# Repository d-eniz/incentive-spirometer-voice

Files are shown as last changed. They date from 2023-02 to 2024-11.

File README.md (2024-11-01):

# Arduino-Enabled Incentive Spirometer with Voice Feedback

This project is an Arduino-enabled incentive spirometer designed specifically for partially sighted users. It utilizes an ultrasonic sensor and the Talkie speech synthesis library to provide real-time voice feedback, making it accessible for individuals who cannot read the device. The system measures the user's inhalation speed and provides audio instructions to encourage effective use.

## Features

- Measures inhalation speed using an ultrasonic sensor.
- Provides voice feedback:
  - **"Safe Speed"** when the inhalation rate is stable.
  - **"Slow Down"** if the inhalation is too fast.
  - **"Speed Up"** if the inhalation is too slow.
- Easy-to-read documentation and making instructions included.

## Hardware Requirements

- Arduino board
- Ultrasonic sensor (HC-SR04 or similar)
- Button (for triggering measurements)
- Speaker (for voice output)
- Talkie library (included in the code for voice synthesis)

Detailed hardware requirements can be found in the [making instructions](./documentation/Making%20Instructions.pdf).

## Installation

1. Clone or download the repository to your local machine.
2. Ensure you have the [Talkie](https://github.com/going-digital/Talkie) library installed in your Arduino IDE.
3. Connect the components as follows:
   - **Trigger Pin**: Digital pin 11
   - **Echo Pin**: Digital pin 12
   - **Switch Pin**: Digital pin 2 (configured with internal pull-up)
4. Upload the code to your Arduino board.

## Usage

1. Press the button connected to `switchPin` to start the spirometer.
2. The system will begin measuring inhalation speed and providing verbal feedback.
3. Based on the inhalation speed, the system will announce:
   - "Safe Speed" when the inhalation is at an appropriate rate.
   - "Slow Down" if the inhalation is too fast.
   - "Speed Up" if the inhalation is too slow.

4. View additional information in the included easy-read guide and follow the audio user instructions for further assistance.

## Documentation

Comprehensive documentation is available, including:
- [Making instructions](./documentation/Making%20Instructions.pdf) for assembly and setup.
- An [easy-read guide](./documentation/Easy%20Read%20guide.pdf) for understanding the device and its use.
- [Audio user instructions](./documentation/Audio%20User%20instructions.mp3) for hands-on support.

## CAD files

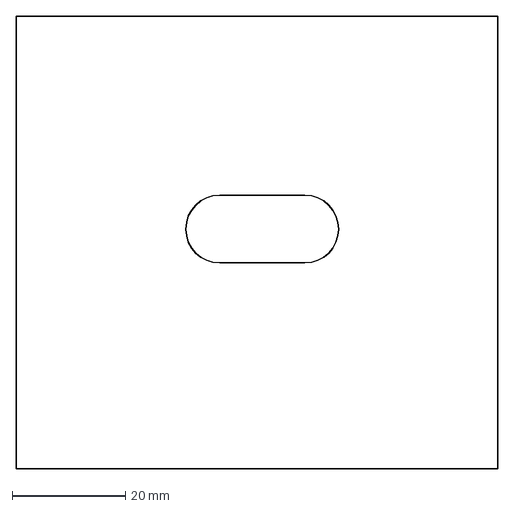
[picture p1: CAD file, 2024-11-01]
dxf/Speaker side.dxf
85.0 x 80.0 mm

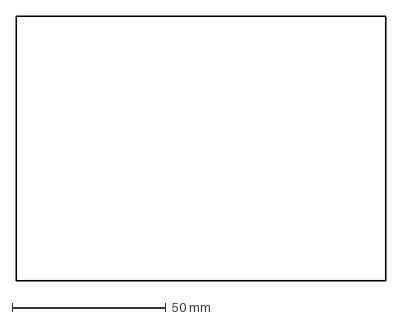
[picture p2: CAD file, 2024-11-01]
dxf/Rectangle sides.dxf
120.0 x 86.0 mm

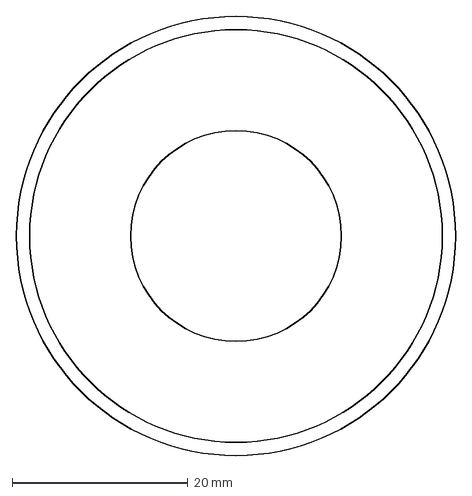
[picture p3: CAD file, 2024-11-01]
dxf/Chamber acrylic donut.dxf
50.0 x 50.0 mm

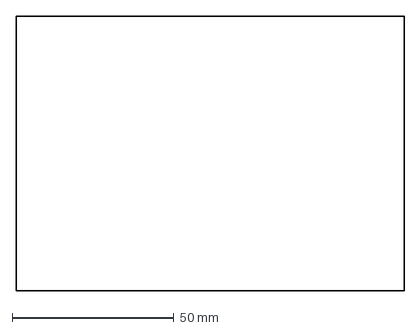
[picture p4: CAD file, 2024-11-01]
dxf/Bottom.dxf
120.0 x 85.0 mm

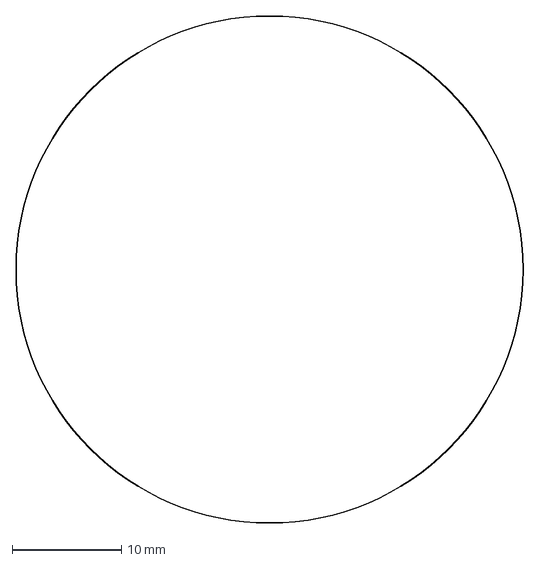
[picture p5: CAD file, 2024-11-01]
dxf/Disc.dxf
46.5 x 46.5 mm

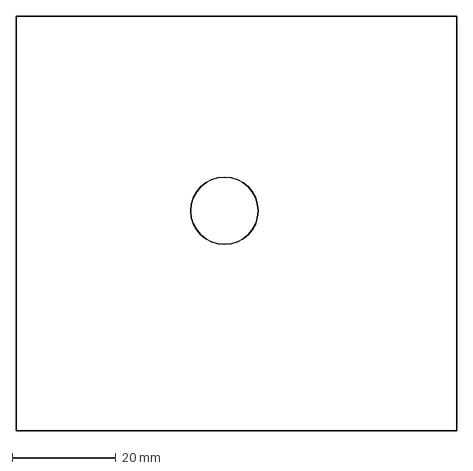
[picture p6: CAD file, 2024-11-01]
dxf/Switch side.dxf
85.0 x 80.0 mm

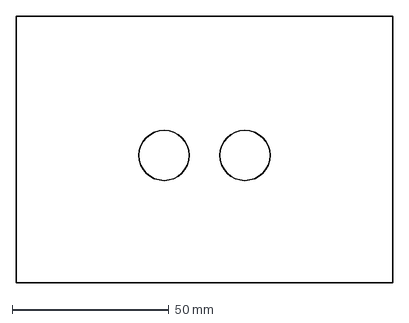
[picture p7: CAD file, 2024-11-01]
dxf/Lid.dxf
120.0 x 85.0 mm

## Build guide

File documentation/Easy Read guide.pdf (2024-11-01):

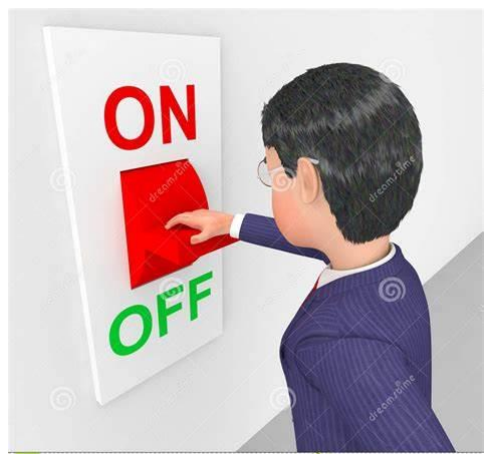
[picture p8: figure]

Switch on the device.

The switch can be found
attached to the black box.

If the device beeps, it is on.

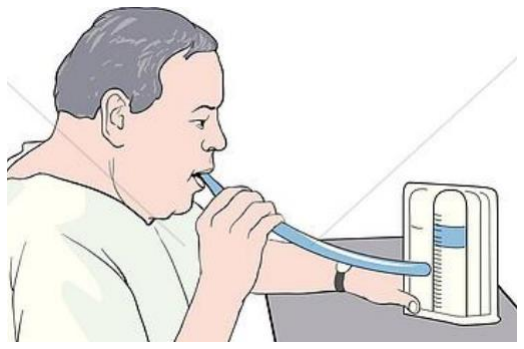
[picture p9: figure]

Place lips on the mouthpiece.

Wait for the voice to say “start”.

Then breathe in for 4 seconds.

Inhale at a steady rate for 4 seconds.

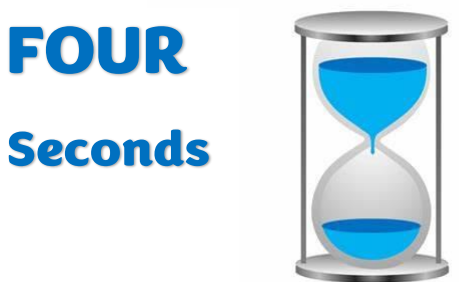
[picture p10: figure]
FOUR; Seconds

After 4 seconds another voice should be heard.

The audio will state the volume of air inhaled in millilitres.

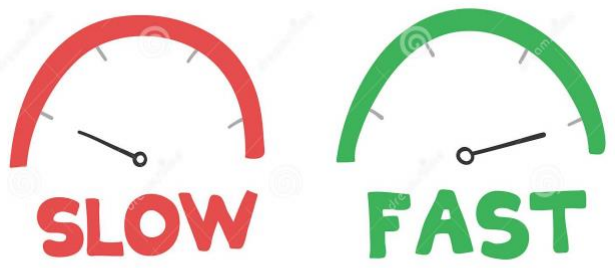
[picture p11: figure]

After this another audio will be heard.

Slow breathing = “speed up”

Steady Breathing = “safe speed”

Fast breathing = “slow down”

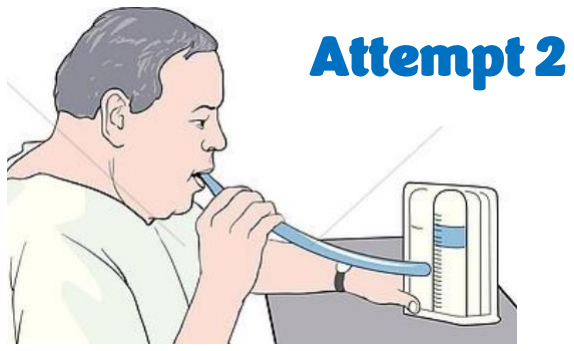
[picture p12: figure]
Attempt 2

If your result was not “safe speed” you can try again.

If the result was “too slow” try and breathe in faster.

If the result was “too fast” try and breath in slower.

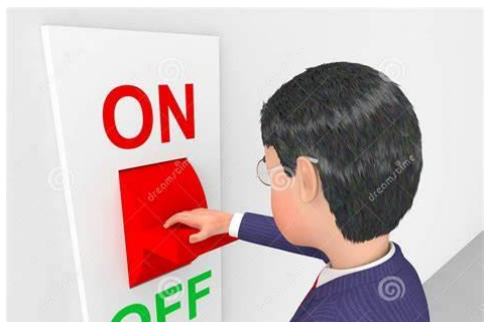
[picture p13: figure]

When finished using, switch off the device.

The switch button is attached to the black box.

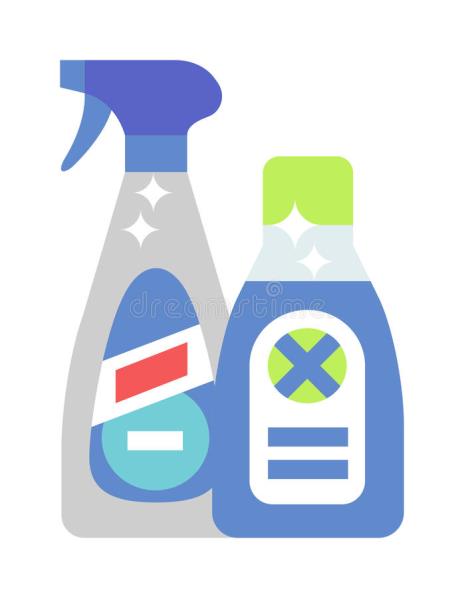
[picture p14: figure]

After finished using, clean the mouthpiece.

Do this by taking out the flexible mouthpiece from the lid.

Use disinfected solution to rinse the mouthpiece for 15 minutes.

Wait for this to dry.

Wipe the device with alcohol wipes.

Do this to remove bacteria.

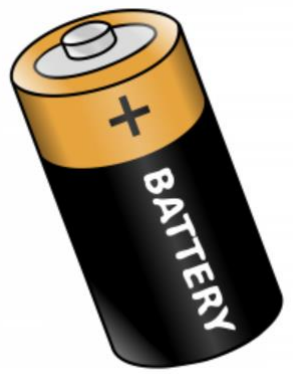
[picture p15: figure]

When the battery runs out
replace it.

Do this by removing the present battery found in the black box.

Then place in the new battery.

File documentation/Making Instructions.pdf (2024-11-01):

Part 1 - CAD
1.1 - Download all provided DXF files.
1.2 - Upload the DXF files to Illustrator and modify them so that all outlines are red and 0.001mm thick - then, print to laser cutting software. The following pieces should be cut:
- Bottom x 1
- Lid x 1
- Chamber acrylic donut x 1
- Rectangle sides x 2
- Speaker side x 1
- Switch side x 1
- Disc x 6

Part 2 - Electronics and Software

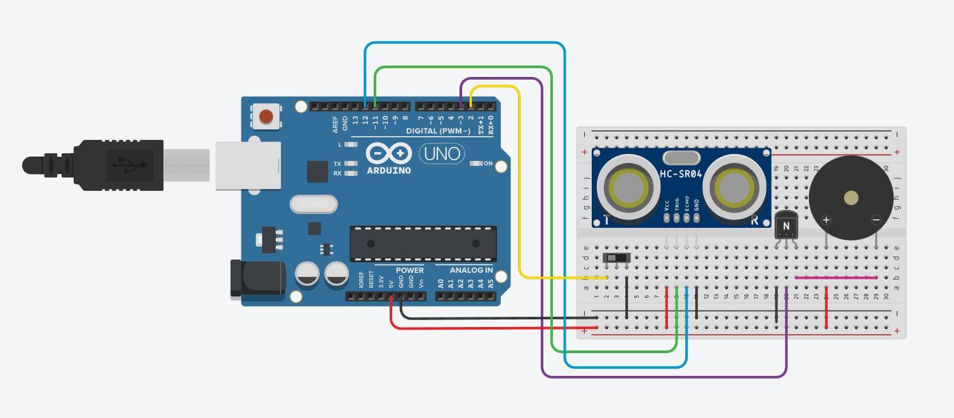
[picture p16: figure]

Required materials:
- Computer with Arduino IDE installed
- Arduino Uno
- Breadboard
- Wires
- HC-SR04 Ultrasonic Distance Sensor
- Speaker driver
- NPN transistor
- Toggle switch
- 9V battery and adapter
- USB type A to B cable

2.1 - Use the circuit diagram and connect every component to the breadboard accordingly. 2.2 - Connect Arduino Uno into computer and run Arduino IDE.
2.3 - Download Talkie: https://github.com/adafruit/Talkie
2.4 - Click Sketch > Include Library > Add .ZIP Library… and choose Talkie-master.zip 2.5 - Copy the following code and paste into Arduino IDE.

2.6 - Copy code version 3.2.0 from the following repository: https://github.com/aribaza/scenario-6/blob/main/V3.2.0
2.6 - Upload the code into the board. Once uploaded, disconnect the Arduino Uno.

Part 3 - Manufacturing
Required materials:
- Laser cutter
- Hack saw
- Saw workbench with clamps
- Hot glue gun
- Epoxy resin
- Scissors
- Sandpaper
- Velcro strips
- Opaque 3mm acrylic plate
- GEVACRIL D=50x47mm L=2000mm Polycarbonate Tube
- Flexible PVC pipe
3.1 - Retrieve laser cut pieces from step 1.
3.2 - The laser cutter will have cut six identical discs. Stack the discs individually, applying a very thin layer of hot glue between them. There should ideally be no spacing between each disc layer. Secure the discs with clamps and let them dry, ensuring that the discs are aligned and don’t stick out. Once cooled, sand the edges.
3.3 - Assemble the box in reference to the CAD file. Use hot glue to seal the edges. Leave out one of the 120x85mm “Rectangle sides.dxf” side plates for now.
3.4 - Cut four 3x120mm velcro strips and stick them on the open side of the box and the remaining plate. This should allow for the side plate to detach and reattach.
3.5 - Get GEVACRIL D=50x47mm L=2000mm Polycarbonate Tube. Using a ruler measure out the 28cm point from the edge and mark it along the tube using a pen. Clamp the tube and cut through the mark. Sand down the sharp edge of the new 28cm tube using sandpaper.
3.6 - Using epoxy resin, join the acrylic disc piece with the hole to the 28cm tube.
3.7 - Place the stacked disks inside the tube, and join the empty side of the tube with the top part of the box. Centre the two holes in the acrylic plate with the tube.
3.8 - Using hot glue, secure the ultrasonic sensor in the box. The receiver and the emitter of the sensor should be sticking up to the tube from the holes in the acrylic plates.
3.9 - Using hot glue, secure the speaker in the oval hole in the side of the box.
3.10 - Unscrew the nut on the toggle switch, stick the switch from inside of the box through the the designated hole on the side of the box and secure from the outside using the nut.,
3.11 - Put the 9V battery into the adapter and connect the adapter to the Arduino.
3.12 - Insert flexible mouth tube into acrylic donut

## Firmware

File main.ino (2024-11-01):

#include "talkie.h"

int trigPin = 11;    // Trigger
int echoPin = 12;    // Echo
long duration, cm, inches;
const int switchPin = 2;
int switchState = HIGH;

Talkie voice;


const uint8_t sp0[] PROGMEM = {0x69,0xFB,0x59,0xDD,0x51,0xD5,0xD7,0xB5,0x6F,0x0A,0x78,0xC0,0x52,0x01,0x0F,0x50,0xAC,0xF6,0xA8,0x16,0x15,0xF2,0x7B,0xEA,0x19,0x47,0xD0,0x64,0xEB,0xAD,0x76,0xB5,0xEB,0xD1,0x96,0x24,0x6E,0x62,0x6D,0x5B,0x1F,0x0A,0xA7,0xB9,0xC5,0xAB,0xFD,0x1A,0x62,0xF0,0xF0,0xE2,0x6C,0x73,0x1C,0x73,0x52,0x1D,0x19,0x94,0x6F,0xCE,0x7D,0xED,0x6B,0xD9,0x82,0xDC,0x48,0xC7,0x2E,0x71,0x8B,0xBB,0xDF,0xFF,0x1F};
const uint8_t sp1[] PROGMEM = {0x66,0x4E,0xA8,0x7A,0x8D,0xED,0xC4,0xB5,0xCD,0x89,0xD4,0xBC,0xA2,0xDB,0xD1,0x27,0xBE,0x33,0x4C,0xD9,0x4F,0x9B,0x4D,0x57,0x8A,0x76,0xBE,0xF5,0xA9,0xAA,0x2E,0x4F,0xD5,0xCD,0xB7,0xD9,0x43,0x5B,0x87,0x13,0x4C,0x0D,0xA7,0x75,0xAB,0x7B,0x3E,0xE3,0x19,0x6F,0x7F,0xA7,0xA7,0xF9,0xD0,0x30,0x5B,0x1D,0x9E,0x9A,0x34,0x44,0xBC,0xB6,0x7D,0xFE,0x1F};
const uint8_t sp2[]  PROGMEM = {0x06,0xB8,0x59,0x34,0x00,0x27,0xD6,0x38,0x60,0x58,0xD3,0x91,0x55,0x2D,0xAA,0x65,0x9D,0x4F,0xD1,0xB8,0x39,0x17,0x67,0xBF,0xC5,0xAE,0x5A,0x1D,0xB5,0x7A,0x06,0xF6,0xA9,0x7D,0x9D,0xD2,0x6C,0x55,0xA5,0x26,0x75,0xC9,0x9B,0xDF,0xFC,0x6E,0x0E,0x63,0x3A,0x34,0x70,0xAF,0x3E,0xFF,0x1F};
const uint8_t sp3[] PROGMEM = {0x0C,0xE8,0x2E,0x94,0x01,0x4D,0xBA,0x4A,0x40,0x03,0x16,0x68,0x69,0x36,0x1C,0xE9,0xBA,0xB8,0xE5,0x39,0x70,0x72,0x84,0xDB,0x51,0xA4,0xA8,0x4E,0xA3,0xC9,0x77,0xB1,0xCA,0xD6,0x52,0xA8,0x71,0xED,0x2A,0x7B,0x4B,0xA6,0xE0,0x37,0xB7,0x5A,0xDD,0x48,0x8E,0x94,0xF1,0x64,0xCE,0x6D,0x19,0x55,0x91,0xBC,0x6E,0xD7,0xAD,0x1E,0xF5,0xAA,0x77,0x7A,0xC6,0x70,0x22,0xCD,0xC7,0xF9,0x89,0xCF,0xFF,0x03};
const uint8_t sp4[] PROGMEM = {0x08,0x68,0x21,0x0D,0x03,0x1C,0x90,0xC0,0x88,0x92,0xB2,0x29,0x87,0x76,0x2B,0x2D,0x5C,0x7B,0x06,0xD9,0xED,0x74,0x64,0x51,0x54,0x4D,0xA2,0xBA,0x99,0xB7,0x3A,0xF8,0xEA,0x74,0xCA,0xD3,0x87,0xBE,0x94,0x3D,0xA4,0xD4,0x4E,0xC9,0x5F,0xF7,0x72,0xA7,0x9C,0x1C,0x63,0xDE,0xF2,0x9B,0xBE,0x34,0x84,0x27,0x2D,0x4B,0xF8,0x53,0x09,0x9C,0x0E,0xB7,0xEE,0xCB,0x5B,0x70,0xDD,0xB2,0xFC,0x3F};
const uint8_t sp5[] PROGMEM = {0x08,0x68,0x4E,0x9D,0x02,0x1C,0x60,0xC0,0x8C,0x69,0x12,0xB0,0xC0,0x28,0xAB,0x8C,0x9C,0xC0,0x2D,0xBB,0x38,0x79,0x31,0x15,0xA3,0xB6,0xE4,0x16,0xB7,0xDC,0xF5,0x6E,0x57,0xDF,0x54,0x5B,0x85,0xBE,0xD9,0xE3,0x5C,0xC6,0xD6,0x6D,0xB1,0xA5,0xBF,0x99,0x5B,0x3B,0x5A,0x30,0x09,0xAF,0x2F,0xED,0xEC,0x31,0xC4,0x5C,0xBE,0xD6,0x33,0xDD,0xAD,0x88,0x87,0xE2,0xD2,0xF2,0xF4,0xE0,0x16,0x2A,0xB2,0xE3,0x63,0x1F,0xF9,0xF0,0xE7,0xFF,0x01};
const uint8_t sp6[] PROGMEM = {0x04,0xF8,0xB9,0x55,0x01,0xBF,0xA5,0x1B,0xE0,0x37,0x0F,0x03,0xFC,0x96,0x61,0x80,0xDF,0x3C,0x0C,0xF0,0x93,0xDA,0x4A,0x87,0x49,0x53,0x91,0x37,0x2B,0x6D,0xD2,0x55,0x23,0xDE,0xAC,0xAA,0xB9,0x16,0x09,0xFF,0xB2,0xFA,0x66,0x93,0x3C,0x63,0xF3,0x9C,0x10,0x38,0x45,0xA9,0x0A,0xD5,0x00,0x00,0x02,0x14,0x97,0xAA,0x80,0xAB,0x6B,0x0D,0xF0,0x63,0xA5,0x01,0x7E,0xCB,0x30,0xC0,0x6F,0xE9,0x0A,0xF8,0x25,0x93,0x01,0x3F,0x57,0xFC,0x3F};
const uint8_t sp7[] PROGMEM = {0x0C,0x78,0xC6,0x95,0x01,0x3F,0xA5,0x28,0xE0,0xB7,0x52,0x0B,0x04,0xE0,0xB7,0x54,0x07,0xFC,0x52,0x66,0x80,0x9F,0xCB,0x56,0x59,0x6C,0x98,0x47,0x3E,0x59,0x4D,0x89,0x69,0x66,0xB9,0x7A,0x34,0x39,0x86,0x9B,0xD9,0xA6,0xD4,0xE7,0x10,0xAE,0xCA,0xAD,0x47,0x97,0x5D,0x9A,0xA9,0xAE,0x1A,0x75,0xB1,0xA5,0x66,0xF9,0xB2,0xD4,0x4D,0x63,0xB6,0x84,0x9A,0x52,0x76,0x45,0x11,0x1A,0xAA,0x4B,0x31,0x0C,0x79,0x4A,0xB0,0x49,0xC5,0x50,0xA2,0x41,0xA1,0xC9,0x65,0xD9,0xAB,0x89,0x56,0x84,0xFF,0x07};
const uint8_t sp8[] PROGMEM = {0xAD,0x1B,0xDE,0x58,0x23,0x17,0xAF,0x6E,0xE8,0x20,0xEB,0x5C,0xBC,0xEA,0x61,0x03,0xAD,0x73,0xF6,0xAA,0x66,0x4A,0xD0,0xCC,0xD9,0xAB,0x1E,0x45,0xC1,0xA3,0x66,0xAF,0x61,0x36,0x03,0x8B,0x5A,0x9C,0xA6,0x51,0x04,0xA2,0x66,0x96,0xBB,0xBA,0x47,0xEC,0xED,0x8A,0x08,0x9C,0xA2,0x54,0x85,0x6A,0x00,0x80,0x02,0x86,0x74,0x63,0xC0,0xE6,0x6A,0xFF,0x0F};
const uint8_t sp9[] PROGMEM = {0x62,0x75,0xDC,0x33,0xB5,0x62,0xB9,0x25,0x0B,0x8E,0x34,0x8F,0xD3,0xA6,0xAE,0x59,0xD2,0x34,0xE9,0x18,0x87,0x27,0xC9,0xD0,0x78,0xAB,0x6F,0xCE,0xC2,0x45,0x1B,0xAF,0xB6,0xF8,0x51,0x73,0x9D,0xB3,0x9A,0x12,0xC7,0x2C,0x6D,0xC9,0xAA,0x73,0x4B,0xF3,0x88,0x26,0xAB,0xCE,0x2D,0xCC,0x23,0xEA,0xAC,0x26,0xB7,0xD0,0x88,0x98,0xB3,0xBA,0x5C,0x43,0x32,0x7D,0xCE,0x1A,0x4A,0x0A,0xCD,0xF4,0x39,0x6B,0xAA,0x3E,0x24,0xCB,0x67,0xAF,0xB5,0xD9,0xE4,0x18,0x5F,0xB4,0xF6,0x6E,0x92,0x62,0x7D,0xD1,0x38,0xBA,0x09,0xF2,0x8D,0x59,0xED,0xE8,0x3A,0xD8,0x27,0x16,0xA6,0xBB,0x7B,0xF2,0x74,0x4F,0x92,0x9E,0x1E,0xC8,0x4A,0xC3,0x49,0x7A,0x9A,0x25,0x2B,0xF5,0x24,0xE9,0xEE,0xD1,0x24,0x25,0x27,0xBA,0xBB,0x25,0x51,0xD3,0xAA,0x24,0xAE,0x5E,0x54,0x55,0x3A,0xD4,0xFF,0x03};
const uint8_t sp10[] PROGMEM = {0x0A,0xD8,0x5C,0x4D,0x03,0x2B,0xAB,0x5E,0xC4,0x33,0x2B,0xAF,0x62,0x84,0x12,0x0D,0x7B,0xB3,0xCA,0x66,0x43,0xA2,0xE3,0xF6,0xAA,0xAA,0x4E,0xC9,0x89,0xDB,0xAB,0x6E,0xBA,0xC5,0xDB,0x66,0xAF,0xB9,0xE8,0xE6,0x4C,0xBF,0x3D,0xE6,0x6A,0xC4,0x4B,0xCA,0x49,0xD9,0xBA,0x61,0x2B,0x09,0x25,0xED,0xE8,0x5A,0xB4,0xC4,0xED,0xA6,0x6B,0x18,0xE1,0x56,0xB7,0x9A,0xAE,0xA6,0x44,0x47,0xDC,0x6E,0xBE,0xC2,0xDD,0xA5,0xF0,0xB8,0xD9,0xFD,0x7F};
const uint8_t sp11[] PROGMEM = {0x29,0x6F,0x52,0xA8,0xBB,0x6A,0x8F,0xBA,0x2B,0xC5,0xE8,0x9C,0xBD,0xAA,0x61,0x1D,0xB5,0xE3,0xF1,0xAA,0x9A,0x35,0xB6,0xB0,0xC5,0xAB,0x5E,0x44,0x53,0x4D,0xBA,0xAD,0x7A,0x42,0x1B,0xE1,0x5C,0xB3,0x9A,0x09,0x6D,0x94,0x62,0xE9,0x6A,0x8A,0x6A,0x37,0x8D,0xC7,0xAB,0x69,0xBC,0xDD,0xCC,0x5F,0xAF,0xB6,0xC9,0x76,0x37,0x7F,0xBD,0xDA,0x62,0xCA,0xDD,0x62,0xD1,0xEA,0xB2,0xCB,0x70,0xA3,0x45,0x69,0xCA,0x36,0xDD,0x14,0x1B,0xAE,0xBE,0x98,0x74,0x33,0x5E,0x39,0xFA,0x6C,0xC3,0x42,0xFC,0xF1,0xE8,0x8B,0x2E,0x71,0x8D,0xDB,0x63,0xA8,0x1A,0xAB,0x39,0x9C,0x8C,0xBE,0x69,0xCA,0xD2,0x50,0x32,0xFA,0xA6,0xD8,0x4B,0x52,0x71,0xEB,0xAA,0xE4,0x28,0x4E,0xD5,0xAD,0xCB,0xC2,0x3C,0x35,0x1D,0xB5,0x36,0xDB,0x14,0xAB,0x8C,0xF4,0xFF};
const uint8_t sp12[] PROGMEM = {0x09,0x98,0xDA,0x22,0x01,0x37,0x78,0x1A,0x20,0x85,0xD1,0x50,0x3A,0x33,0x11,0x81,0x5D,0x5B,0x95,0xD4,0x44,0x04,0x76,0x9D,0xD5,0xA9,0x3A,0xAB,0xF0,0xA1,0x3E,0xB7,0xBA,0xD5,0xA9,0x2B,0xEB,0xCC,0xA0,0x3E,0xB7,0xBD,0xC3,0x5A,0x3B,0xC8,0x69,0x67,0xBD,0xFB,0xE8,0x67,0xBF,0xCA,0x9D,0xE9,0x74,0x08,0xE7,0xCE,0x77,0x78,0x06,0x89,0x32,0x57,0xD6,0xF1,0xF1,0x8F,0x7D,0xFE,0x1F};
const uint8_t sp13[] PROGMEM = {0x08,0x18,0xA2,0x12,0x03,0x18,0x40,0xC0,0x50,0x13,0x25,0x1D,0x3A,0x55,0x9D,0x5B,0xAF,0xAA,0xAB,0x74,0x4A,0xE9,0xB6,0xAA,0x6A,0xC7,0xA0,0xDD,0xDD,0xA8,0xAA,0x1F,0x82,0x75,0xED,0xA5,0x2A,0x8D,0x31,0xC6,0xB3,0x21,0x70,0x8A,0x52,0x15,0xAA,0x01,0x00,0x10,0x80,0xED,0x2C,0x12,0x70,0x53,0x55,0x00,0x66,0x2E,0x1D,0xD9,0x8C,0x46,0x14,0xB9,0x64,0xD5,0xD3,0x1B,0xD2,0xD4,0xAC,0xD1,0x2E,0x6B,0x44,0x9B,0xA5,0x46,0xBF,0xAC,0x91,0x6E,0x04,0x19,0xE3,0xD2,0x4A,0x76,0x6E,0xA4,0x2D,0xCB,0x2A,0xC9,0x65,0xE8,0xB6,0x0D,0x29,0x6C,0xEB,0xA1,0xC3,0xD1,0x1D,0x54,0xB9,0x28,0x75,0x67,0xB7,0x90,0xE5,0x6A,0x27,0xDC,0xDD,0xA1,0xB7,0xB9,0x92,0xF2,0x77,0x1B,0x1C,0x92,0x0D,0xDD,0xDF,0x92,0x9A,0x59,0x55,0xFC,0x7F};
const uint8_t sp14[] PROGMEM = {0x08,0xE8,0x2A,0x94,0x00,0xC3,0x56,0x10,0x60,0xFA,0x0A,0x01,0x4C,0x97,0xAE,0x80,0x66,0xCB,0x4A,0x6F,0xF3,0x84,0xB1,0xB4,0x6E,0x9D,0x73,0x57,0x1A,0xD0,0x6E,0x74,0xC1,0x7D,0x71,0x61,0xD6,0x51,0x07,0xF7,0x26,0x25,0xDE,0x46,0x15,0xED,0x52,0x37,0xFB,0x29,0x65,0x1E,0x18,0x61,0xD6,0x1A,0x81,0x53,0x94,0xAA,0x50,0x0D,0x00,0x80,0x02,0x2C,0xE3,0x5E,0x80,0x13,0xBA,0x13,0x30,0x43,0xDB,0x2A,0x46,0x34,0xA2,0x8E,0xC5,0xAB,0x9A,0xDE,0x88,0x2E,0x4A,0xAD,0x7A,0x7A,0x25,0x7E,0x0F,0xB2,0xDA,0x69,0x84,0xED,0xC4,0xEC,0xEA,0xA6,0x15,0xF6,0x53,0xB1,0x6B,0x18,0x56,0x38,0x4F,0xCC,0x8D,0x71,0x5A,0x61,0x7F,0x35,0x3A,0xC6,0xA1,0x44,0xFC,0xCD,0x74,0x9B,0xBA,0xC1,0xCA,0x54,0xAB,0x6D,0x6C,0x06,0x3B,0x5D,0xED,0xB4,0xA1,0x29,0x6A,0x37,0x57,0xDD,0x86,0x2A,0xA9,0x52,0x43,0x51,0xEB,0xAA,0x0E,0x8E,0xA8,0x48,0xFF,0x0F};
const uint8_t sp15[] PROGMEM = {0x02,0x68,0xD6,0xCC,0x00,0x43,0x9A,0x39,0x60,0x3A,0xF7,0x51,0x34,0x5B,0x6A,0x2C,0x6D,0x4E,0xD5,0x92,0x99,0x89,0x2C,0x39,0x55,0xF3,0xAE,0xA6,0x32,0x67,0x54,0xC5,0x99,0xB9,0xC8,0x1C,0x07,0x0C,0xA5,0x94,0x01,0x04,0x4E,0x51,0xAA,0x42,0x35,0x00,0x02,0xB0,0x84,0x4A,0x6B,0x4F,0x6C,0x23,0x15,0x2F,0x6D,0x18,0xC1,0x44,0xC2,0x17,0x8F,0x69,0xBA,0x54,0xA8,0x58,0x3D,0xE6,0x6D,0x53,0xA1,0x73,0xF5,0x5A,0xA6,0x31,0xA2,0x8D,0x89,0x63,0x9D,0xCE,0x88,0xD6,0x47,0xB6,0x75,0x5B,0x13,0x6C,0xAF,0x54,0x96,0x61,0x84,0x22,0x64,0x74,0x59,0x9A,0x61,0x4B,0x0D,0xA7,0x65,0x6A,0x86,0xD2,0x23,0x5C,0xA7,0xB1,0x08,0xCA,0xB0,0x70,0x9D,0x86,0xA2,0x38,0xC9,0xA2,0x55,0xE8,0x32,0x11,0x8F,0x94,0xD6,0xFF,0x0F};
const uint8_t sp16[] PROGMEM = {0x0C,0x78,0xC6,0x95,0x01,0x3F,0xA5,0x28,0xE0,0xB7,0x52,0x0B,0x04,0xE0,0xB7,0x54,0x07,0xFC,0x52,0x66,0x80,0x9F,0xCB,0x96,0xB7,0xA5,0x1B,0x9B,0x66,0x5A,0x59,0xB3,0x26,0x1A,0xF6,0xA6,0x15,0xCD,0x2B,0x59,0xFA,0x6A,0x04,0x4E,0x51,0xAA,0x42,0x35,0x40,0x01,0x25,0xA7,0x24,0xE0,0x98,0x1E,0x07,0xFC,0x9D,0x2E,0x80,0x57,0x9D,0x18,0xB0,0x05,0x6A,0x02,0xAE,0x54,0x1D,0x6D,0x77,0xCA,0xEA,0xF9,0x78,0xF5,0xD3,0x1A,0x51,0xE7,0xE2,0x35,0x4F,0x6F,0xC4,0x53,0x93,0xC6,0x3A,0x9D,0x91,0x6C,0x86,0x6A,0xC7,0x34,0x2A,0x7A,0x66,0x36,0x9D,0xD3,0xA9,0xC8,0x99,0xD5,0x72,0x75,0xC7,0x92,0xA3,0x96,0xC3,0xD3,0x3D,0x46,0xA4,0x3A,0x09,0x4F,0x73,0x98,0xE1,0xEA,0x24,0x3C,0xDD,0x92,0x87,0xBB,0x93,0xF4,0x0D,0x63,0x94,0x2E,0x75,0xFF,0x1F};
const uint8_t sp17[] PROGMEM = {0x0C,0xF8,0x29,0x45,0x01,0xBF,0x95,0x5A,0x20,0x00,0xBF,0xA5,0x3A,0xE0,0x97,0x32,0x03,0xFC,0x5C,0xB6,0xAA,0x26,0x53,0xD5,0x7D,0xF5,0x6A,0x8A,0x4E,0xB5,0xCC,0x47,0xAB,0xAB,0xAA,0xD4,0xC2,0x36,0xA7,0x31,0xF9,0x30,0x33,0x49,0x9D,0x86,0x6C,0xD5,0x5D,0xA4,0xF5,0xE8,0xAB,0x32,0x37,0x97,0x95,0x69,0xA8,0x0A,0x7B,0x50,0xD5,0xA5,0xA1,0x69,0xA8,0x56,0x63,0x1B,0xC6,0xA6,0xB1,0x43,0xD4,0x35,0x24,0xE0,0x18,0xB3,0x96,0xAF,0xBC,0x99,0x86,0x9A,0x5A,0xD5,0x2C,0x71,0xD6,0xC4,0x5C,0xF5,0x2C,0x4E,0x94,0x31,0x6B,0x35,0x33,0x1A,0xF2,0x64,0xE9,0xD5,0x4F,0xAF,0xA8,0x1B,0x81,0xC7,0xBC,0xAC,0x91,0x9E,0x1B,0x29,0xDB,0x32,0x8A,0x7A,0x19,0xA8,0xEC,0x43,0x08,0xC5,0xB9,0xE9,0xF4,0x34,0x0D,0x35,0xAE,0x76,0xD3,0x5B,0x14,0x76,0xA9,0x3B,0x4A,0x7F,0x77,0x58,0xA1,0xE6,0x38,0xFD,0xDD,0x51,0x9A,0xBB,0xAB,0xF4,0x57,0x67,0x16,0xDA,0xB3,0xFE,0x1F};
const uint8_t sp18[] PROGMEM = {0x6B,0x18,0x36,0x88,0x3B,0x1B,0xEF,0x61,0x0D,0xD3,0x27,0x52,0xE5,0x9A,0x51,0x8F,0x1E,0xC8,0x96,0x4B,0x5A,0xD5,0x03,0x61,0xD5,0xCC,0x72,0x75,0x35,0x10,0xD3,0x13,0x11,0x81,0x53,0x94,0xAA,0x50,0x0D,0x80,0x02,0x2C,0x95,0x5A,0x80,0x17,0xC7,0x57,0x3E,0xBD,0x33,0x6B,0x36,0x59,0xD5,0xC8,0x4E,0xE4,0xB9,0x64,0xD5,0x33,0x24,0x61,0xE7,0xA4,0x35,0x2C,0xEF,0x28,0x9B,0xA5,0xC6,0x38,0x9D,0xA2,0x5F,0x84,0x6E,0xCB,0x74,0x8A,0x7E,0x6E,0xA6,0xEC,0xCD,0xB0,0x76,0x4B,0xD4,0x72,0x74,0x87,0x1E,0xA9,0x76,0xD2,0x3D,0x3C,0x59,0x84,0x26,0x4D,0x4F,0xD3,0x68,0x15,0xEE,0xE4,0xFF,0x01};
const uint8_t sp19[] PROGMEM = {0x6E,0x2F,0x44,0xB4,0x5B,0x93,0xA6,0xAD,0x32,0x96,0x2E,0x69,0xBA,0x96,0x26,0xD3,0xCC,0x65,0xF1,0x1A,0x9B,0x9C,0xE0,0xD4,0x2D,0x6B,0x68,0xA6,0xCD,0xCA,0x56,0xAF,0xAE,0xB9,0x64,0x6F,0x5F,0xB4,0xEA,0xE6,0x84,0xA7,0xA3,0x52,0xAB,0x5B,0x40,0xAB,0x28,0xD3,0xAE,0xCD,0x0A,0xC7,0x5D,0x35,0x23,0x70,0x8A,0x52,0x15,0xAA,0x01,0x50,0x80,0xAB,0x4C,0x0A,0xB0,0x7C,0x4B,0xCB,0x57,0xDE,0x4C,0x43,0x4D,0xAD,0x6A,0x96,0x38,0x6B,0x62,0xAE,0x7A,0x16,0x27,0xCA,0x98,0xB5,0x9A,0x19,0x0D,0x79,0xB2,0xF4,0xEA,0xA7,0x57,0xD4,0x8D,0xC0,0x63,0x5E,0xD6,0x48,0xCF,0x8D,0x94,0x6D,0x19,0x45,0xBD,0x0C,0x54,0xF6,0x21,0x84,0xE2,0xDC,0x74,0x79,0x9A,0x86,0x1A,0x57,0xBB,0xE5,0x2D,0x0A,0xBB,0xD4,0x1D,0x95,0xBF,0x3B,0xAC,0x50,0x73,0x5C,0xFE,0xEE,0x28,0xCD,0xDD,0x55,0xF8,0xAB,0x33,0x0B,0xED,0x59,0xFF,0x0F};
const uint8_t sp20[] PROGMEM = {0x0A,0xE8,0x4A,0xCD,0x01,0xDB,0xB9,0x33,0xC0,0xA6,0x54,0x0C,0xA4,0x34,0xD9,0xF2,0x0A,0x6C,0xBB,0xB3,0x53,0x0E,0x5D,0xA6,0x25,0x9B,0x6F,0x75,0xCA,0x61,0x52,0xDC,0x74,0x49,0xA9,0x8A,0xC4,0x76,0x4D,0xD7,0xB1,0x76,0xC0,0x55,0xA6,0x65,0xD8,0x26,0x99,0x5C,0x56,0xAD,0xB9,0x25,0x23,0xD5,0x7C,0x32,0x96,0xE9,0x9B,0x20,0x7D,0xCB,0x3C,0xFA,0x55,0xAE,0x99,0x1A,0x30,0xFC,0x4B,0x3C,0xFF,0x1F};
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

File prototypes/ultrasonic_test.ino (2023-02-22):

int trigPin = 11;    // Trigger
int echoPin = 12;    // Echo
long duration, cm, inches;
const int buzzer = 9;

void setup() {
  //Serial Port begin
  Serial.begin (9600);
  //Define inputs and outputs
  pinMode(trigPin, OUTPUT);
  pinMode(echoPin, INPUT);
  pinMode(buzzer, OUTPUT);
}

void loop() {
  // Wait until the object is further than 4cm away
  while (true) {
    digitalWrite(trigPin, LOW);
    delayMicroseconds(5);
    digitalWrite(trigPin, HIGH);
    delayMicroseconds(10);
    digitalWrite(trigPin, LOW);
    duration = pulseIn(echoPin, HIGH);
    cm = (duration/2) / 29.1;
    if (cm > 4) {
      break;
    }
  }

  // Record for 4 seconds
  long startTime = millis();
  long endTime = startTime + 4000;
  int numReadings = 0;
  long totalDistance = 0;
  while (millis() < endTime) {
    digitalWrite(trigPin, LOW);
    delayMicroseconds(5);
    digitalWrite(trigPin, HIGH);
    delayMicroseconds(10);
    digitalWrite(trigPin, LOW);
    duration = pulseIn(echoPin, HIGH);
    cm = (duration/2) / 29.1;
    totalDistance += cm;
    numReadings++;
    delay(50); // Wait for 50ms before taking the next reading
  }

  // Calculate and display the final value
  cm = totalDistance / numReadings;
  Serial.print("Final distance: ");
  Serial.print(cm);
  Serial.print("cm");
  Serial.println();
  tone(buzzer,cm*100);

  delay(1000); // Wait for 1 second before taking another measurement
}

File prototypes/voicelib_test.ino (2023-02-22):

#include "talkie.h"

int trigPin = 11;    // Trigger
int echoPin = 12;    // Echo
long duration, cm, inches;

Talkie voice;

const uint8_t spDANGER[] PROGMEM = {0x2D, 0xBF, 0x21, 0x92, 0x59, 0xB4, 0x9F, 0xA2, 0x87, 0x10, 0x8E, 0xDC, 0x72, 0xAB, 0x5B, 0x9D, 0x62, 0xA6, 0x42, 0x9E, 0x9C, 0xB8, 0xB3, 0x95, 0x0D, 0xAF, 0x14, 0x15, 0xA5, 0x47, 0xDE, 0x1D, 0x7A, 0x78, 0x3A, 0x49, 0x65, 0x55, 0xD0, 0x5E, 0xAE, 0x3A, 0xB5, 0x53, 0x93, 0x88, 0x65, 0xE2, 0x00, 0xEC, 0x9A, 0xEA, 0x80, 0x65, 0x82, 0xC7, 0xD8, 0x63, 0x0A, 0x9A, 0x65, 0x5D, 0x53, 0xC9, 0x49, 0x5C, 0xE1, 0x7D, 0x2F, 0x73, 0x2F, 0x47, 0x59, 0xC2, 0xDE, 0x9A, 0x27, 0x5F, 0xF1, 0x8B, 0xDF, 0xFF, 0x03};
const uint8_t spMOTOR[]  PROGMEM = {0x66, 0xAA, 0x8C, 0x69, 0x53, 0x92, 0xC4, 0x2D, 0x2F, 0x6B, 0x2A, 0x74, 0xDA, 0x9D, 0xB2, 0xDD, 0xF6, 0x36, 0xAB, 0xCE, 0x78, 0xDA, 0x9D, 0xB2, 0xD5, 0x9A, 0x01, 0xDB, 0x77, 0x45, 0xA0, 0x75, 0xC5, 0xB8, 0x71, 0x59, 0xDA, 0x31, 0xE5, 0x6A, 0x22, 0x63, 0xDE, 0xDA, 0x9A, 0xBB, 0xA3, 0x75, 0x68, 0xAF, 0x7B, 0x3E, 0xC3, 0x9D, 0x97, 0x60, 0x87, 0xE6, 0x8B, 0x4F, 0x78, 0x4B, 0x76, 0xB2, 0x09, 0xAF, 0xFE, 0xFD, 0x7F};
const uint8_t spFIRE[]   PROGMEM = {0x04, 0x18, 0xCE, 0x4D, 0x02, 0x1A, 0xD0, 0x80, 0x04, 0x46, 0x91, 0x55, 0x57, 0x07, 0x6D, 0xD9, 0xCD, 0xAE, 0x4F, 0x55, 0x5D, 0x59, 0x87, 0xAE, 0xB9, 0xD5, 0x6D, 0x5B, 0xDB, 0x7D, 0x93, 0xB6, 0xED, 0xEE, 0xE3, 0x5A, 0x6B, 0x6A, 0xF4, 0x91, 0xD5, 0x73, 0x6B, 0x67, 0xF5, 0x47, 0xBC, 0xD4, 0xA7, 0x9C, 0xA5, 0x34, 0xE4, 0xD0, 0xA6, 0xF0, 0xE4, 0xAA, 0xB8, 0x2D, 0xAB, 0xC3, 0x9B, 0x62, 0xC2, 0xAC, 0x74, 0xF6, 0x9F, 0xFB, 0x72, 0x0B, 0xEC, 0x92, 0xCD, 0xEE, 0xCF, 0x43, 0x69, 0x4C, 0x5B, 0xFF, 0x3F};
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
